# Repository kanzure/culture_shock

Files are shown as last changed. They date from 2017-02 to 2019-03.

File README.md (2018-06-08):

Table of Contents
=================

* [This repository documents how to use and make an electroporator.](#this-repository-documents-how-to-use-and-make-an-electroporator)
* [Now to describe the project directory and how to use it.](#now-to-describe-the-project-directory-and-how-to-use-it)
* [The Project Schematic Representation](#the-project-schematic-representation)
* [The Project Physical Design Representation](#the-project-physical-design-representation)
* [Running code on the Culture Shock platform(s)](#running-code-on-the-culture-shock-platforms)
* [Project Module Standard](#project-module-standard)
* [Using Culture Shock and Steps Leading up to Transformation](#using-culture-shock-and-steps-leading-up-to-transformation)
* [Aiding with Development and Debug](#aiding-with-development-and-debug)
* [Miscellany](#miscellany)

## This repository documents how to use and make an electroporator.

Cloning this repo gives you [ documentation on lab technique ](LAB_MANUAL.md) and [using culture shock,](USING_CULTURE_SHOCK.md) plus a project directory for making printed circuits
and related parts of an **electroporator**, a machine for transforming bacterial suspensions in water to become a new GMO.  For how to use culture shock, see [Using Culture Shock and Steps Leading up to Transformation](#using-culture-shock-and-steps-leading-up-to-transformation).  For how to make your own, or something new based on Culture Shock hardware, read on below.

The **culture shock** electroporator needs some care in using to avoid electrocution hazards -- it may not work out to borrow just some of this project and turn it on -- it really needs its insulating housing to be safe.

## Now to describe the project directory and how to use it.
You will notice files that end with .lht or .gvp .sch .bom.
Those hold the primary data to generate pcb fab files, or to reuse the circuits to make something else with this as a starting point.  

## The Project Schematic Representation
The schematic representations of the printed circuits that make up culture shock are edited with the **gschem program** from the free open source software, (FOSS), project called gEDA   Schematic files end in **.sch,** -- for example kvboard.sch.
* howtos here: [http://wiki.evilmadscientist.com/GEDA_Resources](http://wiki.evilmadscientist.com/GEDA_Resources)
* and [http://wiki.geda-project.org/geda:documentation](http://wiki.geda-project.org/geda:documentation)

## The Project Physical Design Representation
The **.lht files** hold layout data edited with the **pcb-rnd** FOSS program from here:  
	http://repo.hu/projects/pcb-rnd/	
If it's your first time using pcb or pcb-rnd, start from the begining with this tutorial for **pcb**, which **pcb-rnd** is derived from:  
	http://www.delorie.com/pcb/docs/gs/gs.html
	
To take a *quick look* at the state of things without needing to learn to edit them, you can look at image files of the schematics and layout with any browser.
Look in directory hardware_schematics_layouts for these files:  kvboard.lht.png kvboard.sch.png pyflex_f401.sch.png pyflex_f401.lht pyflex_f401_boost.sch.png.
To get ability to zoomin and also edit the schematics and layout, install the software as below on a debian testing installation.  It can be easy to start using those schematic and pcb editors -- just give these commands:

```bash
sudo apt-get update
sudo apt-get install geda
sudo apt-get install pcb-rnd
```

then run these commands from the project subdirectory hardware_schematics_layouts created by cloning the **culture shock** repo:
```bash
pcb-rnd kvboard.lht
pcb-rnd micropulser.lht
gschem kvboard.sch micropulser.sch
```
The schematic and netlist and layout tools used are from the gEDA code: http://wiki.evilmadscientist.com/GEDA_Resources#Basics

## Running code on the Culture Shock platform(s)
There are two MCU platforms now -- G30TH is phasing out of use, and PYFLEX_F401 is starting up:
* a board called g30pulser.sch runs with the micropython platform definition called G30TH
  * [Instructions to flash MicroPython for the G30TH version of culture_shock are here](DEVELOPER_NOTE.md#flashing-micropython)
  * [Additional notes are here (TODO: compress into a single document)](micropython_STM32F4_coding/micropython_compile_G30TH.txt)
* and a board called pyflex_f401.sch runs with the micropython platform definition called PYFLEX_F401.
  * PYFLEX_F401 is complete now, so compile micropython with platform PYFLEX_F401.
  * Very soon, instructions for compiling microptyhon programs for culture shock's PYFLEX_F401 platform will be written.

When you connect the culture_shock USB cable to your computer, it will now appear as a "USB mass storage" device.
Now you can simply copy the Python (.py) files to the "USB mass storage" drive/folder.
* For G30TH based copy the .Py files here: [g30_mcu_code](g30_mcu_code) 

The PYFLEX_F401 platform for micropython has the **STM32F401CE** MCU
* voltage converter from USB 5V or battery 3.2 volts up to 18VDC
* voltage converter from USB 5V down to lithium iron phosphate battery charging at 3.2 volts.
* 2 20 pin flat flex connectors to get to the GPIOs, ADCs, battery and com ports of the MCU
* a microUSB AB connector for charging
* a microUSB AB connector for development and data logging data transfer
* A 2-wire I2C port can be used with OLED and LCD displays.
* planned mode to precharge ONBOARD_18V and be ready tp fire a shot, then go back to standby after a minute. (not implemented yet)

## Project Module Standard
Flat flex cables, (FFCs), can be symmetric, their connectors are symmetric, and so connection signal vs. pin number order can be reversed by ordinary use of cables and connectors.  Using symmetric straight through flat flex cables and connectors is the standard for this project because it simplifies early design prototypes by allowing them to lay flat on the bench with component side of all modules up where one can see and probe them.  What symmetric and straight through means by example is: starting with a FFC connector with pins 1 thru 20 with a dot near pin 1 signals connect to another board by going through pin 1 on the first board, straight across without cables being folded or flipped over and into pin 20 of the other board. Pin 2 of the FFC connector on the first board leads to pin 19 on the 2nd, etc.

## Using Culture Shock and Steps Leading up to Transformation
Prepare growth media, purify plasmid DNA from a bacterial culture -- [Lab Manual.md](LAB_MANUAL.md), then transform E.Coli by electroporation -- [ Using Culture Shock](USING_CULTURE_SHOCK.md).

## Aiding Development and Debugging
See [Developer's Manual](DEVELOPER_NOTE.md) to get started with the culture shock and micropython GIT repositories on github, and hook up to culture shock so you can give it commands.

## Miscellany
The repo's `.gitignore` file is set to skip git tracking of `.jpg` (photos) and `.pdf` (datasheets) and zipped file bundles, so any of them to distribute need to be saved outside the git repo as a zip file.

Seeing a preview of markdown files like this README.md helps speed documenation.  This previewer is useful:  [grip markdown viewer](https://github.com/joeyespo/grip)  Grip can serve more than one file at a time with this syntax:  grip README.md 6150  grip LAB_MANUAL.md 6151.  Doing that helps edit files like this one, (with many links to other files).

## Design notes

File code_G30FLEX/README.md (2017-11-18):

First, before starting, the MCU board must have micropython loaded -- see other docs 
such as micropython_compile_G30TH.txt, micropython_coding_with_rshell.txt about that.

To run code on a culture shock board, (with STM32F401 inside), several files are needed.

As this code is written so far, it needs these files loaded to the flash filesystem of the 
micropython running MCU:

* tim3_enable_tim1_tim2_tim5__tim1_shuts_down.py
* stm_low_level.py
* nvic.py
* boot.py
* ssd1306.py
  * (__OPTIONAL__) for 0.96" 128x64 OLED support

After loading those files and resetting the MCU board, the tim3_enable_tim1_tim2_tim5__tim1_shuts_down.py
program will run.

For a serial prompt:
 - Windows: you need to go to 'Device manager', right click on the unknown device,
   then update the driver software, using the 'pybcdc.inf' file found on this drive.
   Then use a terminal program like Hyperterminal or putty.
 - Mac OS X: use the command: screen /dev/tty.usbmodem*
 - Linux: use the command: screen /dev/ttyACM0

Please visit http://micropython.org/help/ for further help.

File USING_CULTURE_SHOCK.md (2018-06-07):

# Using Culture Shock v0.5 first article prototype
###  Intro
  The  v0.5 first article prototype has  no buttons -- all commands are done via a command line over the USB serial port.  
  New scripts to run are loaded by writing files to the culture shock using the USB port virtual file system files located at:
  * Windows, Linux, Mac: folder called PYBFLASH in the popup window for a USB drive when culture shock data USB cable plug is plugged into the USB port of a laptop.

  * Debian Linux:  /username/media/PYBFLASH directory

The project github repository, (that this document is part of), is the source of scripts to run for basic testing and as a starting point for your new recipes. The folder to find code in is: [code_PYFLEX_F401  ](https://github.com/kanzure/culture_shock/tree/master/code_PYFLEX_F401    "Culture Shock micropython code")   

####

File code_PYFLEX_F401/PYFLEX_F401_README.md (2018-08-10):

First, before starting, the MCU board must have micropython loaded -- see other docs 
such as micropython_compile_G30TH.txt, micropython_coding_with_rshell.txt about that.

To run code on a culture shock board, (with STM32F401 inside), several files are needed.

As this code is written for v0.5 hardware, it needs these files loaded to the flash filesystem of the 
micropython running MCU:

* pulser_main.py
* stm_low_level.py
* nvic.py
* boot.py
* ssd1306.py
  * (__OPTIONAL__) for 0.96" 128x64 OLED support

After loading those files and resetting the MCU board, the program called by boot.py will run.

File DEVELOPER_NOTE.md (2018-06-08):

Table of Contents
=================

* [GIT workflow methods](#git-workflow-methods)
  * [Setting up your GIT clone with collaborators:](#setting-up-your-git-clone-with-collaborators)
  * [reset a collaborator's master to kanzure's master](#reset-a-collaborators-master-to-kanzures-master)
  * [Merging branches (will usually leave a "merge commit" which rebasing can avoid)](#merging-branches-will-usually-leave-a-merge-commit-which-rebasing-can-avoid)
  * [Rebasing branches](#rebasing-branches)
     * [Squashing commits with rebase](#squashing-commits-with-rebase)
  * [Setup better git difftool/mergetool](#setup-better-git-difftoolmergetool)
* [Creating table-of-contents for MarkDown (.md) files](#creating-table-of-contents-for-markdown-md-files)
* [Preview MarkDown files locally before commit/push to GitHub](#preview-markdown-files-locally-before-commitpush-to-github)
* [Getting a micropython prompt on the USB serial port](#getting-a-micropython-prompt-on-the-usb-serial-port)
* [Self-Test Idea](#self-test-idea)
  * [Debug setup](#debug-setup)
  * [ADC pulse viewer GUI](#adc-pulse-viewer-gui)
  * [ADC graphing on OLED display](#adc-graphing-on-oled-display)
* [MicroPython C Modules](#micropython-c-modules)
* [Flashing MicroPython](#flashing-micropython)
  * [G30TH](#g30th)
* [ADC DMA ideas](#adc-dma-ideas)
  * [STM selected documentation](#stm-selected-documentation)
  * [Registers](#registers)
     * [11.12.1 ADC status register (ADC_SR)](#11121-adc-status-register-adc_sr)
     * [11.12.2 ADC control register 1 (ADC_CR1)](#11122-adc-control-register-1-adc_cr1)
     * [11.12.3 ADC control register 2 (ADC_CR2)](#11123-adc-control-register-2-adc_cr2)

# GIT workflow methods
## Setting up your GIT clone with collaborators:
* Adding a collaborator's github URL
  * ```bash
    git remote add collaborator https://github.com/<collaborator_username>/culture_shock.git
    git fetch collaborator
    ```

## reset a collaborator's master to kanzure's master
based on this StackOverflow (https://stackoverflow.com/a/39628366/253127)

* add the original (kanzure's) repo:
  * `git remote add original https://github.com/kanzure/culture_shock.git`
* Fetch the latest changes from the collaborator
  * `git fetch original`
* Checkout your __local__ master branch
  * `git checkout master`
* reset master to original's version, so your files match theirs exactly
  * `git reset --hard original/master`

## Merging branches (will usually leave a "merge commit" which rebasing can avoid)
* Fetch the latest changes from the collaborator
  * `git fetch collaborator`
* Merge the collaborator's changes (from master branch)
  * `git merge collaborator/master`

## Rebasing branches 
* Fetch the latest changes from the collaborator
  * `git fetch collaborator`
* Checkout the collaborator's changes (from master branch)
  * `git checkout collaborator/master`
* Depending on if merge conflicts are expected
  * If not, then use __non-interactive__ rebasing
    * `git rebase master`
  * If yes (or you want to squash/edit their commits/commit-messages), then use __interactive__ rebasing
    * `git rebase -i master`
* If there are merge conflicts
  * show the files in question
    * `git status`
  * use git's mergetool to see the your changes and their changes side-by-side
    * single file
      * `git mergetool path/to/file_of_interest`
    * all files in question
      * `git mergetool`
* Create a temporary branch for safety
  * `git checkout -b mergeme`
* Go back to __your__ last version of __master__ branch
  * `git checkout master`
* Merge your rebased changes into master
  * `git merge mergeme`

### Squashing commits with rebase
* I am currently using this method during debugging of the MarkDown syntax used for this note
  * ```
    git add DEVELOPER_NOTE.md
    git commit -m "sqsh"
    git rebase -i HEAD~2
    ```
* the last command allows you to modify whether the last (2) commits are applied, how they are applied, in what order
* I see the following output
  * ```
    pick 12e8eee added notes for syncing with other github 'forks' (collaborators)
    pick 7f7aedb sqsh
    
    # Rebase aebf933..7f7aedb onto aebf933 (2 command(s))
    #
    # Commands:
    # p, pick = use commit
    # r, reword = use commit, but edit the commit message
    # e, edit = use commit, but stop for amending
    # s, squash = use commit, but meld into previous commit
    # f, fixup = like "squash", but discard this commit's log message
    # x, exec = run command (the rest of the line) using shell
    # d, drop = remove commit
    #
    # These lines can be re-ordered; they are executed from top to bottom.
    #
    # If you remove a line here THAT COMMIT WILL BE LOST.
    #
    # However, if you remove everything, the rebase will be aborted.
    #
    # Note that empty commits are commented out
    ```
* I would then edit the second line to read
  * `s 7f7aedb sqsh`
  * This squashes the commit into the previous (commit above it)
    * the goal is to merge the commit-contents into the previous commit, but hide the fact that the contents actually came from more than one commit (squashing all changes into a single commit)
* save the text file
* now rebase will open the commit-message, showing all the combined messages
  * ```
    # This is a combination of 2 commits.
    # The first commit's message is:
    
    added notes for syncing with other github 'forks' (collaborators)
    
    # This is the 2nd commit message:
    
    sqsh
    
    # Please enter the commit message for your changes. Lines starting
    # with '#' will be ignored, and an empty message aborts the commit.
    # interactive rebase in progress; onto 7120033
    # Last commands done (2 commands done):
    #    pick 3a59de4 added notes for syncing with other github 'forks' (collaborators)
    #    s 63cf084 sqsh
    # No commands remaining.
    # You are currently rebasing branch 'master' on '7120033'.
    #
    # Changes to be committed:
    #       modified:   DEVELOPER_NOTE.md
    ```
  * remove the line starting with
    * `sqsh`
* save and exit the commit-message
* Done!
  * continue working, push, etc
    * during this debug cycle, because I continually edit the MarkDown, then squash, to test the web-browser rendering I then have to run a `git push -f` to force-push and overwrite the previous commit I made, because it was already made public

## Setup better git difftool/mergetool
* What look to be pretty good notes here:
  * https://gist.github.com/karenyyng/f19ff75c60f18b4b8149#file-git_mergetool_tutorial-md
* Setting a specific mergetool/difftool which is already supported by git
  * from: https://stackoverflow.com/a/6412645/253127
  * example of open-source tools supported
    * kdiff3, kompare, tkdiff, meld, xxdiff, emerge, vimdiff, gvimdiff, ecmerge, diffuse, opendiff, p4merge and araxis
  * add the following lines to your `~/.gitconfig`
    * ```
      [diff]
          tool = meld
      ```
* Setting up mergetool/difftool that isn't supported
  * the stackoverflow linked from the prev also works, but looks to be a less-concise copy of this
    * see "Git 1.7.x and older" section
      * https://www.scootersoftware.com/support.php?zz=kb_vcs#gitlinux

# Creating table-of-contents for MarkDown (.md) files
* get this handy TOC generator
  * `git clone https://github.com/ekalinin/github-markdown-toc`
* cd to the __culture_shock__ repo, then run the TOC generator on the .md file of interest
  * `cd culture_shock`
  * `../github-markdown-toc/gh-md-toc DEVELOPER_NOTE.md`
* paste the output into the .md file
* commit and push

# Preview MarkDown files locally before commit/push to GitHub
* Download `grip` with `pip`
  * `pip install grip`
    * source https://github.com/joeyespo/grip
* `cd` to __culture_shock__ repo
* run `grip`
  * copy the web URL printed on the terminal
    * navigate to it using your web-browser

# Getting a micropython prompt on the USB serial port:
 - Windows: you need to go to 'Device manager', right click on the unknown device,
   then update the driver software, using the 'pybcdc.inf' file found on this drive.
   Then use a terminal program like Hyperterminal or putty.
 - Mac OS X: use the command: screen /dev/tty.usbmodem*
 - Linux: use the command: screen /dev/ttyACM0

 - After you have a prompt, you can tell culture shock to do a soft reset \<ctl\>d or \<ctl\>x to get out of the REPL (read eval print loop) and back to your system command line.  For more on what micropython can do from the REPL, see http://micropython.org/help/ as a starting point.

# Self-Test Idea
* Setup 10 pulses with shortest possible pulse-width
  * setup list `adc_vals`
* Setup ADC timer with same freq as pulses, but out of phase 180°
* setup IRQ function callback on ADC timer, the function will:
  * read the ADC, append to `adc_vals`
* at end of pulse-train, send `adc_vals` out the serial port for printing on the user-terminal

## Debug setup
* PA0 and PA1, as seen here in kvboard v0.1, are the wires for pulsing the switched power supply to get high volts.
![alt text](https://raw.githubusercontent.com/kanzure/culture_shock/0ed7805f742bc01429d4466670109e092e9572f7/hardware_schematics_layouts/kvboard.png "KiloVolt producing circuit-board v0.1 (2017-2-16)")
* Connect your oscilloscope to these pins to watch the pulse widths and periods of each digital operation from the microcontroller
  * These are useful to trigger on
    * you can then watch the analog/choppier high-voltage develop on another oscilloscope input
* With Culture_Shock v0.1, the G30TH module was used for the STM microcontroller it was built with
  * The pinout of the G30TH module is shown here on the right-side
![alt](photos_protos_tests_simuls_sketches/G30TH_module_schematic_PCB_pinout.jpg)
* Connecting the first oscilloscope probe to PA1 and GND (red minigrabber)
  ![alt](photos_protos_tests_simuls_sketches/probing_g30th_pa1_gnd.jpg)
* Connecting the second oscilloscope probe to PA0
  ![alt](photos_protos_tests_simuls_sketches/probing_g30th_pa1_pa0_gnd.jpg)
* Connecting the third oscilloscope probe and 1GOhm resistor to the high-voltage (HV) output
  * 33 kOhm dummy load is used between the HV terminals
  ![alt](photos_protos_tests_simuls_sketches/probing_33k_dummy_load_with_1GOhm.jpg)
* Overall setup
  ![alt](photos_protos_tests_simuls_sketches/probing__overall_setup.jpg)

## ADC pulse viewer GUI
* requires pexpect `pip install pexpect` and tk (comes with Python out-of-box in most cases)
  * pexpect is a terminal interaction library
    * you can send lines to a terminal
    * you setup what you expect the terminal to reply with
      * these act like triggers to tell your program your output was seen
* I used `picocom` for test and development
  * thus what I programmed the <b>expect</b>ations to be might need adjusted for other terminal programs
* the terminal interaction is logged to the command-line where you start the GUI
  * use this to debug why your <b>expect</b>ations aren't being met
* every time the __pulse__ button is clicked, the __a()__ function is called using the 3 input boxes for args
  * reduce the __Num Pulse Pairs__ for a first-try adjustment
    * you should see the waveform get shorter in length
* __NOTE__: this __is__ still __work-in-progress__, dependent on the ADC working, which is still WIP
  * has not been rigourously debugged, understood, or tested with conditions other than the default (starting) conditions for period, width, num-pulses

* see demo pics here
  * https://imgur.com/a/I3CLt
![alt text](https://i.imgur.com/1TSNEN3.gif "ADC reporting waveform to GUI")

## ADC graphing on OLED display
* https://github.com/micropython/micropython/blob/master/drivers/display/ssd1306.py
  * http://docs.micropython.org/en/latest/wipy/library/machine.I2C.html
  * http://docs.micropython.org/en/latest/pyboard/library/framebuf.html
* Graphing the ADC values will require scaling the data to fit.
* Currently with the DMA transfer the ADC reads into a buffer of length 2048.
* The OLED is only 128 wide
  * 64 tall
* scaling in the X direction may be done with averaging every (2048/128)==16 values
  * or a median filter
  * or a max-val filter
* scaling in the Y will use the ADC max-val and the height of the OLED (64)
  * val / 1024.0 * 64.0

* see demo pics here
  * https://imgur.com/a/LBorg

# MicroPython C Modules
In case we really need to customize or reduce overhead
* http://micropython-dev-docs.readthedocs.io/en/latest/adding-module.html

# Flashing MicroPython
## G30TH
* See here for background
  * http://blog.davehylands.com/2016/07/bringing-up-micropython-on-ghi.html
* `git clone https://github.com/micropython/micropython.git`
* `cd micropython`
* `git checkout v1.9.3`
* __patch with ADC DMA sampling changes__
  * `patch -p1 ./ports/stm32/adc.c < ../culture_shock/FOR_ADC_DMA__adc.c.patch`
    * assumes culture_shock and micropython repos are in the same directory
    * hacks the __read_timed__ method, and adds a new method __read_timed_stop__
* `cd ports/stm32/boards/`
* `git clone https://github.com/dhylands/G30TH.git`
* `cd ..`
* connect 3.3V to pin B0
* `make BOARD=G30TH`
* if you need to erase the program area, i.e. if you wrote bad MicroPython code that "bricked" the MCU
  * `dfu-util -v -s :mass-erase:force -a 0 -d 0483:df11 -D build-G30TH/firmware.dfu`
* `make BOARD=G30TH deploy`

# ADC DMA ideas

## STM selected documentation
* 11.8.1 Using the DMA
When the DMA mode is enabled (DMA bit set to 1 in the ADC_CR2 register), after each
conversion of a regular channel, a DMA request is generated. This allows the transfer of the
converted data from the ADC_DR register to the destination location selected by the
software.
Despite this, if data are lost (overrun), the OVR bit in the ADC_SR register is set and an
interrupt is generated (if the OVRIE enable bit is set). DMA transfers are then disabled and
DMA requests are no longer accepted. In this case, if a DMA request is made, the regular
conversion in progress is aborted and further regular triggers are ignored. It is then
necessary to clear the OVR flag and the DMAEN bit in the used DMA stream, and to re-
initialize both the DMA and the ADC to have the wanted converted channel data transferred
to the right memory location. Only then can the conversion be resumed and the data
transfer, enabled again.

## Registers
### 11.12.1 ADC status register (ADC_SR)
5     4     3     2     1     0
OVR   STRT  JSTRT JEOC  EOC   AWD
rc_w0 rc_w0 rc_w0 rc_w0 rc_w0 rc_w0

* Bits 31:6 Reserved, must be kept at reset value.
* Bit 5 OVR: Overrun
  * This bit is set by hardware when data are lost . It is cleared by software. Overrun detection is enabled only when DMA = 1 or EOCS = 1.
    * 0: No overrun occurred
    * 1: Overrun has occurred
* Bit 4 STRT: Regular channel start flag
  * This bit is set by hardware when regular channel conversion starts. It is cleared by software.
    * 0: No regular channel conversion started
    * 1: Regular channel conversion has started
* Bit 3 JSTRT: Injected channel start flag
  * This bit is set by hardware when injected group conversion starts. It is cleared by software.
    * 0: No injected group conversion started
    * 1: Injected group conversion has started
* Bit 2 JEOC: Injected channel end of conversion
  * This bit is set by hardware at the end of the conversion of all injected channels in the group. It is cleared by software.
    * 0: Conversion is not complete
    * 1: Conversion complete
* Bit 1 EOC: Regular channel end of conversion
  * This bit is set by hardware at the end of the conversion of a regular group of channels. It is cleared by software or by reading the ADC_DR register.
    * 0: Conversion not complete (EOCS=0), or sequence of conversions not complete (EOCS=1)
    * 1: Conversion complete (EOCS=0), or sequence of conversions complete (EOCS=1)
* Bit 0 AWD: Analog watchdog flag
  * This bit is set by hardware when the converted voltage crosses the values programmed in the ADC_LTR and ADC_HTR registers. It is cleared by software.
    * 0: No analog watchdog event occurred
    * 1: Analog watchdog event occurred

### 11.12.2 ADC control register 1 (ADC_CR1)
* Address offset: 0x04
* Reset value: 0x0000 0000

* Bit 31 Reserved, must be kept at reset value.
* Bit 30 SWSTART: Start conversion of regular channels
  * This bit is set by software to start conversion and cleared by hardware as soon as the conversion starts.
    * 0: Reset state
    * 1: Starts conversion of regular channels
  * Note: This bit can be set only when ADON = 1 otherwise no conversion is launched.
* Bits 29:28 EXTEN: External trigger enable for regular channels
  * These bits are set and cleared by software to select the external trigger polarity and enable the trigger of a regular group.
    * 00: Trigger detection disabled
    * 01: Trigger detection on the rising edge
    * 10: Trigger detection on the falling edge
    * 11: Trigger detection on both the rising and falling edges
* Bits 27:24 EXTSEL[3:0]: External event select for regular group
  * These bits select the external event used to trigger the start of conversion of a regular group:
    * 0000: Timer 1 CC1 event
    * 0001: Timer 1 CC2 event
    * 0010: Timer 1 CC3 event
    * 0011: Timer 2 CC2 event
    * 0100: Timer 2 CC3 event
    * 0101: Timer 2 CC4 event
    * 0110: Timer 2 TRGO event
    * 0111: Timer 3 CC1 event
    * 1000: Timer 3 TRGO event
    * 1001: Timer 4 CC4 event
    * 1010: Timer 5 CC1 event
    * 1011: Timer 5 CC2 event
    * 1100: Timer 5 CC3 event
    * 1101: Reserved
    * 1110: Reserved
    * 1111: EXTI line11
* Bit 23 Reserved, must be kept at reset value.
* Bit 22 JSWSTART: Start conversion of injected channels
  * This bit is set by software and cleared by hardware as soon as the conversion starts.
    * 0: Reset state
    * 1: Starts conversion of injected channels
  * Note: This bit can be set only when ADON = 1 otherwise no conversion is launched.
* Bits 21:20 JEXTEN: External trigger enable for injected channels
  * These bits are set and cleared by software to select the external trigger polarity and enable the trigger of an injected group.
    * 00: Trigger detection disabled
    * 01: Trigger detection on the rising edge
    * 10: Trigger detection on the falling edge
    * 11: Trigger detection on both the rising and falling edges
* Bits 19:16 JEXTSEL[3:0]: External event select for injected group
  * These bits select the external event used to trigger the start of conversion of an injected group.
    * 0000: Timer 1 CC4 event
    * 0001: Timer 1 TRGO event
    * 0010: Timer 2 CC1 event
    * 0011: Timer 2 TRGO event
    * 0100: Timer 3 CC2 event
    * 0101: Timer 3 CC4 event
    * 0110: Timer 4 CC1 event
    * 0111: Timer 4 CC2 event
    * 1000: Timer 4 CC3 event
    * 1001: Timer 4 TRGO event
    * 1010: Timer 5 CC4 event
    * 1011: Timer 5 TRGO event
    * 1100: Reserved
    * 1101: Reserved
    * 1110: Reserved
    * 1111: EXTI line15
* Bits 15:12 Reserved, must be kept at reset value.
* Bit 11 ALIGN: Data alignment
  * This bit is set and cleared by software. Refer to Figure 35 and Figure 36.
    * 0: Right alignment
    * 1: Left alignment
* Bit 10 EOCS: End of conversion selection
  * This bit is set and cleared by software.
    * 0: The EOC bit is set at the end of each sequence of regular conversions. Overrun detection is enabled only if DMA=1.
    * 1: The EOC bit is set at the end of each regular conversion. Overrun detection is enabled.
* Bit 9 DDS: DMA disable selection (for single ADC mode)
  * This bit is set and cleared by software.
    * 0: No new DMA request is issued after the last transfer (as configured in the DMA controller)
    * 1: DMA requests are issued as long as data are converted and DMA=1
* Bit 8 DMA: Direct memory access mode (for single ADC mode)
  * This bit is set and cleared by software. Refer to the DMA controller chapter for more details.
    * 0: DMA mode disabled
    * 1: DMA mode enabled
* Bits 7:2 Reserved, must be kept at reset value.
* Bit 1 CONT: Continuous conversion
  * This bit is set and cleared by software. If it is set, conversion takes place continuously until it is cleared.
    * 0: Single conversion mode
    * 1: Continuous conversion mode
* Bit 0 ADON: A/D Converter ON / OFF
  * This bit is set and cleared by software.
  * Note:
    * 0: Disable ADC conversion and go to power down mode
    * 1: Enable ADC

### 11.12.3 ADC control register 2 (ADC_CR2)
* Address offset: 0x08
* Reset value: 0x0000 0000
* Bit 31 Reserved, must be kept at reset value.
* Bit 30 SWSTART: Start conversion of regular channels
  * This bit is set by software to start conversion and cleared by hardware as soon as the conversion starts.
    * 0: Reset state
    * 1: Starts conversion of regular channels
  * Note: This bit can be set only when ADON = 1 otherwise no conversion is launched.
* Bits 29:28 EXTEN: External trigger enable for regular channels
  * These bits are set and cleared by software to select the external trigger polarity and enable the trigger of a regular group.
    * 00: Trigger detection disabled
    * 01: Trigger detection on the rising edge
    * 10: Trigger detection on the falling edge
    * 11: Trigger detection on both the rising and falling edges
* Bits 27:24 EXTSEL[3:0]: External event select for regular group
  * These bits select the external event used to trigger the start of conversion of a regular group:
    * 0000: Timer 1 CC1 event
    * 0001: Timer 1 CC2 event
    * 0010: Timer 1 CC3 event
    * 0011: Timer 2 CC2 event
    * 0100: Timer 2 CC3 event
    * 0101: Timer 2 CC4 event
    * 0110: Timer 2 TRGO event
    * 0111: Timer 3 CC1 event
    * 1000: Timer 3 TRGO event
    * 1001: Timer 4 CC4 event
    * 1010: Timer 5 CC1 event
    * 1011: Timer 5 CC2 event
    * 1100: Timer 5 CC3 event
    * 1101: Reserved
    * 1110: Reserved
    * 1111: EXTI line11
* Bit 23 Reserved, must be kept at reset value.
* Bit 22 JSWSTART: Start conversion of injected channels
  * This bit is set by software and cleared by hardware as soon as the conversion starts.
    * 0: Reset state
    * 1: Starts conversion of injected channels
  * Note: This bit can be set only when ADON = 1 otherwise no conversion is launched.
* Bits 21:20 JEXTEN: External trigger enable for injected channels
  * These bits are set and cleared by software to select the external trigger polarity and enable the trigger of an injected group.
    * 00: Trigger detection disabled
    * 01: Trigger detection on the rising edge
    * 10: Trigger detection on the falling edge
    * 11: Trigger detection on both the rising and falling edges
* Bits 19:16 JEXTSEL[3:0]: External event select for injected group
  * These bits select the external event used to trigger the start of conversion of an injected group.
    * 0000: Timer 1 CC4 event
    * 0001: Timer 1 TRGO event
    * 0010: Timer 2 CC1 event
    * 0011: Timer 2 TRGO event
    * 0100: Timer 3 CC2 event
    * 0101: Timer 3 CC4 event
    * 0110: Timer 4 CC1 event
    * 0111: Timer 4 CC2 event
    * 1000: Timer 4 CC3 event
    * 1001: Timer 4 TRGO event
    * 1010: Timer 5 CC4 event
    * 1011: Timer 5 TRGO event
    * 1100: Reserved
    * 1101: Reserved
    * 1110: Reserved
    * 1111: EXTI line15
* Bits 15:12 Reserved, must be kept at reset value.
* Bit 11 ALIGN: Data alignment
  * This bit is set and cleared by software. Refer to Figure 35 and Figure 36.
    * 0: Right alignment
    * 1: Left alignment
* Bit 10 EOCS: End of conversion selection
  * This bit is set and cleared by software.
    * 0: The EOC bit is set at the end of each sequence of regular conversions. Overrun detection is enabled only if DMA=1.
    * 1: The EOC bit is set at the end of each regular conversion. Overrun detection is enabled.
* Bit 9 DDS: DMA disable selection (for single ADC mode)
  * This bit is set and cleared by software.
    * 0: No new DMA request is issued after the last transfer (as configured in the DMA controller)
    * 1: DMA requests are issued as long as data are converted and DMA=1
* Bit 8 DMA: Direct memory access mode (for single ADC mode)
  * This bit is set and cleared by software. Refer to the DMA controller chapter for more details.
    * 0: DMA mode disabled
    * 1: DMA mode enabled
* Bits 7:2 Reserved, must be kept at reset value.
* Bit 1 CONT: Continuous conversion
  * This bit is set and cleared by software. If it is set, conversion takes place continuously until it is cleared.
    * 0: Single conversion mode
    * 1: Continuous conversion mode
* Bit 0 ADON: A/D Converter ON / OFF
  * This bit is set and cleared by software.
  * Note:
    * 0: Disable ADC conversion and go to power down mode
    * 1: Enable ADC

 ### Remaining registers
 * [REGISTER INFO](REGISTER_INFO.md)

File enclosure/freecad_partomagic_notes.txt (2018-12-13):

 
    easyw-fc wrote:
    Hi, when using PoM I can only create nested Parts, but without the option to have more of one Part at the same level... may be I'm not using PoM in the right way...I attach the desired and of the PoM tree I get

PoM always adds whatever is created to active container. Including new Parts. That is, to have "Part002" to "Part", activate "Part" before creating "Part002" by double-clicking it in tree (you can also get there using Leave, Enter buttons of PoM workbench, which I highly recommend adding to a global toolbar, as they are quite versatile).

To add another Part to the root of document, deactivate whatever is active (either by double-clicking it in tree, or pressing Leave button until it becomes grey)

   triplus wrote:
    How about if Tip would have a Compound property. Once enabled Tip would basically become Part -> Make compound feature (making a compound out of individual features inside Module/Body)? I am guessing user could use all sorts of tools already mentioned earlier (and a few others) directly on such Module/Body after?

I'm making a special independent container for that. Do you think I should merge them all into one mighty container? (the benefit of doing that is ability to switch container type after it's been made and populated).
Top

    shaise wrote:
    Then what is the meaning of a Cube inside a Body? (create a cube in Part WB, select it, then press the Body button from PartDesign)

This process imports any type of solid as base feature in a PartDesign body, so you can use PD tools with it.

    shaise wrote:
    I still cant put sketches directly on it

Sure you can, but for some reason PartDesign still considers the cube a "foreign" object. So when trying to map a sketch to the cube, a dialog opens which says that selected geometries are not part of the active body, and to select a type of reference. The first two (Make independent copy/Make dependent copy) create a reference object, but "Create cross-reference" attaches the sketch directly to the cube.

by DeepSOIC » Mon Mar 06, 2017 2:33 pm 

Let's say you are modeling a flange, with a non-circular opening. Lets use a slot. We want screw holes around the opening... 
There is no PartDesign pattern (AFAIR) that can produce the necessary holes, but there is a handy tool in Draft workbench that can help, Draft PathArray. This is where PoM Subtractive Shape comes in.
* Create Subtractive shape container. You will be presented with an empty screen, where you should model the shape that cuts the holes.
* Add shapebinder of the sketch that was padded (select Sketch in tree, and click PoM Shapebinder).
* From Sketcher workbench, create a new sketch, and constrain up a slot that goes through the centers of future screwholes.
* From Part workbench, add a cylinder, and set it up to have the right radius, and enough height to penetrate all the way through. Leave it at the origin
* Select Cylinder, Sketch001, and apply Draft PathArray 
* Done! Leave the container to get back into Body (e.g. use PoM Leave command, or double-click Body in tree).
You may need to click Recompute button to see the result. Also, there is a chance Tip property of SubtractiveShape isn't pointing to the actual shape to use for cutting (PathArray). In that case, you can fix it by using PoM Set as Tip command. 

by DeepSOIC » Tue Mar 07, 2017 2:58 pm 
New feature!
* Exporter
It is an object you add to the project, and it can automatically export an object into a file whenever it changes. It can export Parts and Groups, but limited to a single level nesting (child Part containers are fed to FreeCAD's exporter, but FC's exporters usually ignore them).
I hope that this picture explains well what it does   https://forum.freecadweb.org/download/file.php?id=34489

Exporter checks that model has no features in an error state, will refuse to export if it finds errors.

BLUE = edits

New feature!
* Tree automation
When you enter a container, tree is automatically expanded to show only the stuff in active container. Everything around it is automatically collapsed.

For example. You are in shapegroup deep inside, and you change active container to body. shapegroup is automatically collapsed, and part001 is too, so that the tree view shows the piece you work on in isolation.

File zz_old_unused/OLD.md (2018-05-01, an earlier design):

Old and Unused Directories and Files
=================

* These are Files that were for temporary use in debugging, or somehow are obsolete.
    they might still be useful for supporting existing early prototypes, so this is where to 
    look in that case.

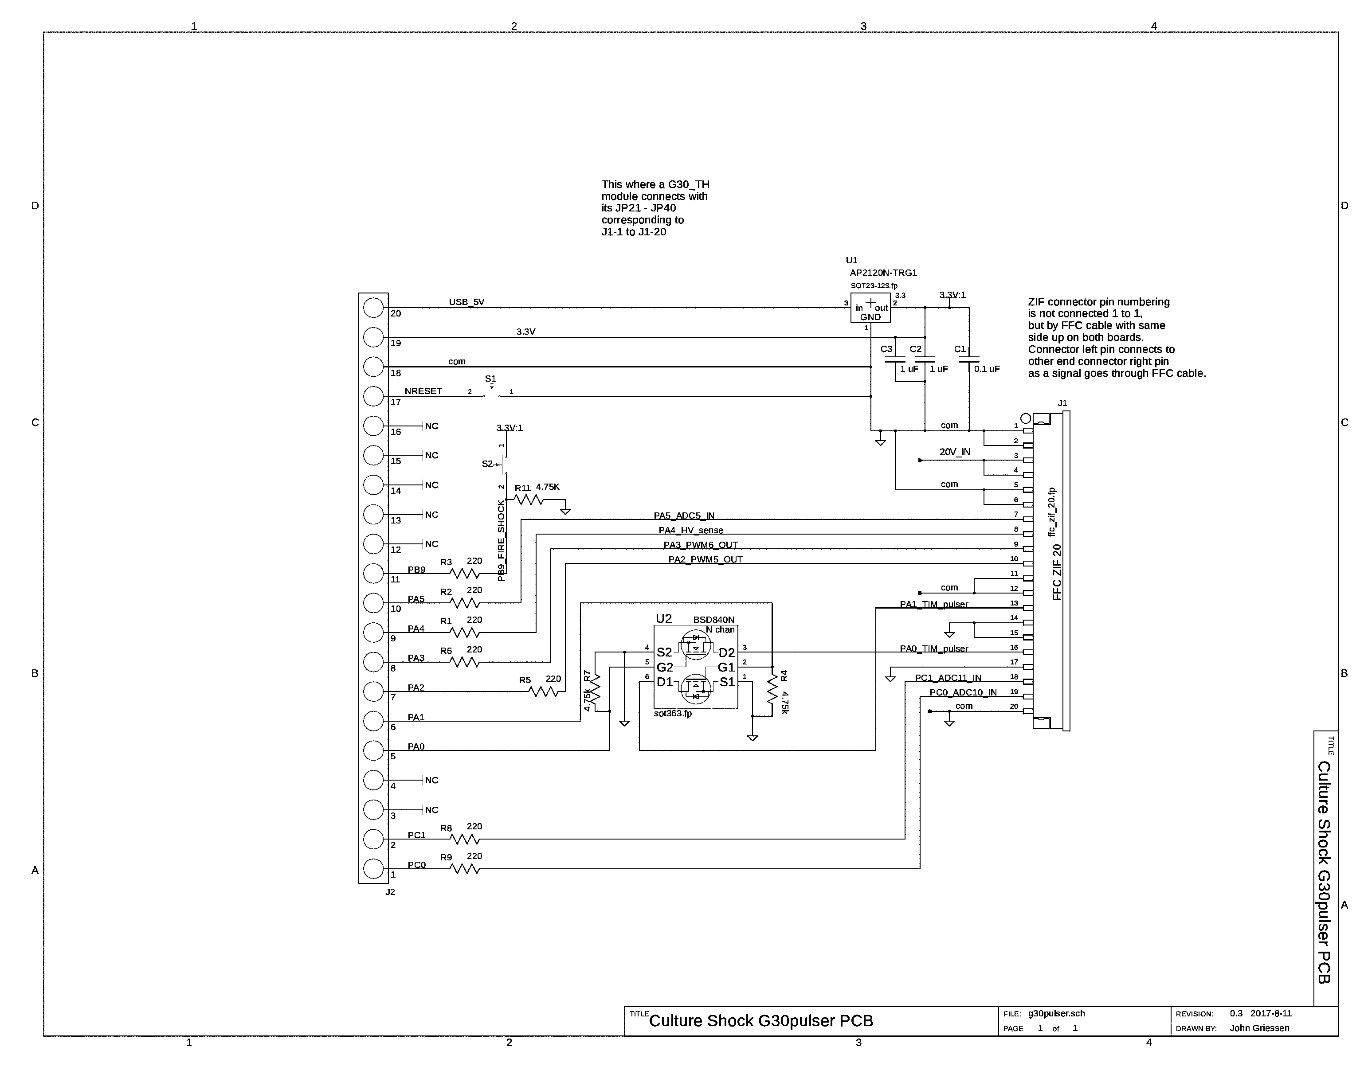
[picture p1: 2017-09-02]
hardware_schematics_layouts/g30pulser-sm.png

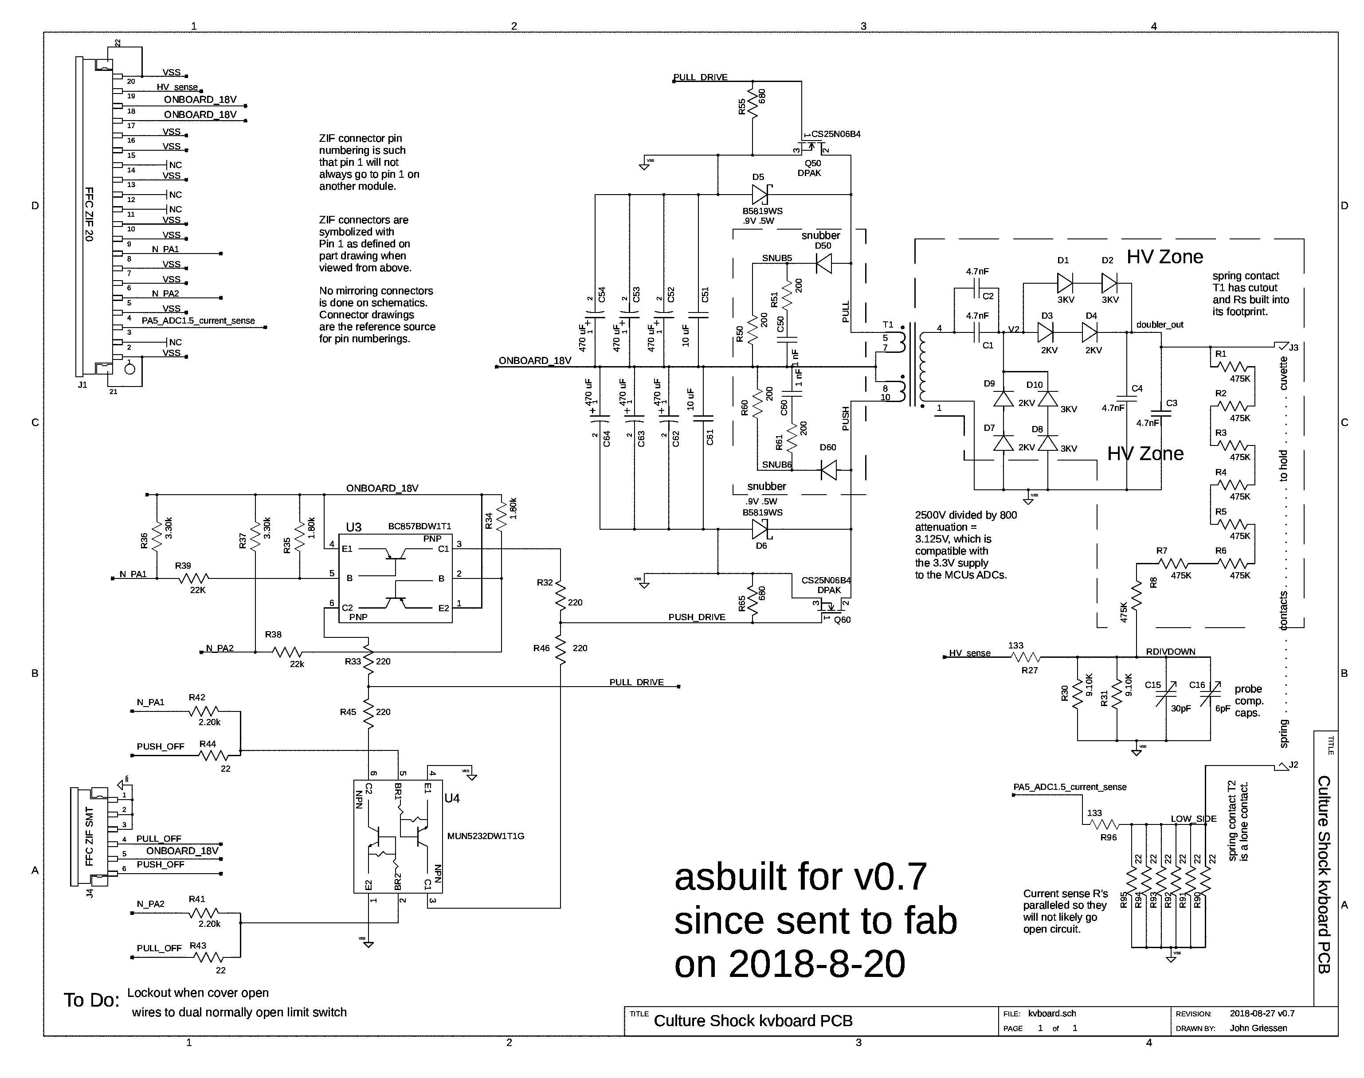
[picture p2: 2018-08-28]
hardware_schematics_layouts/kvboard_asbuilt_v0.7.sch-sm.png

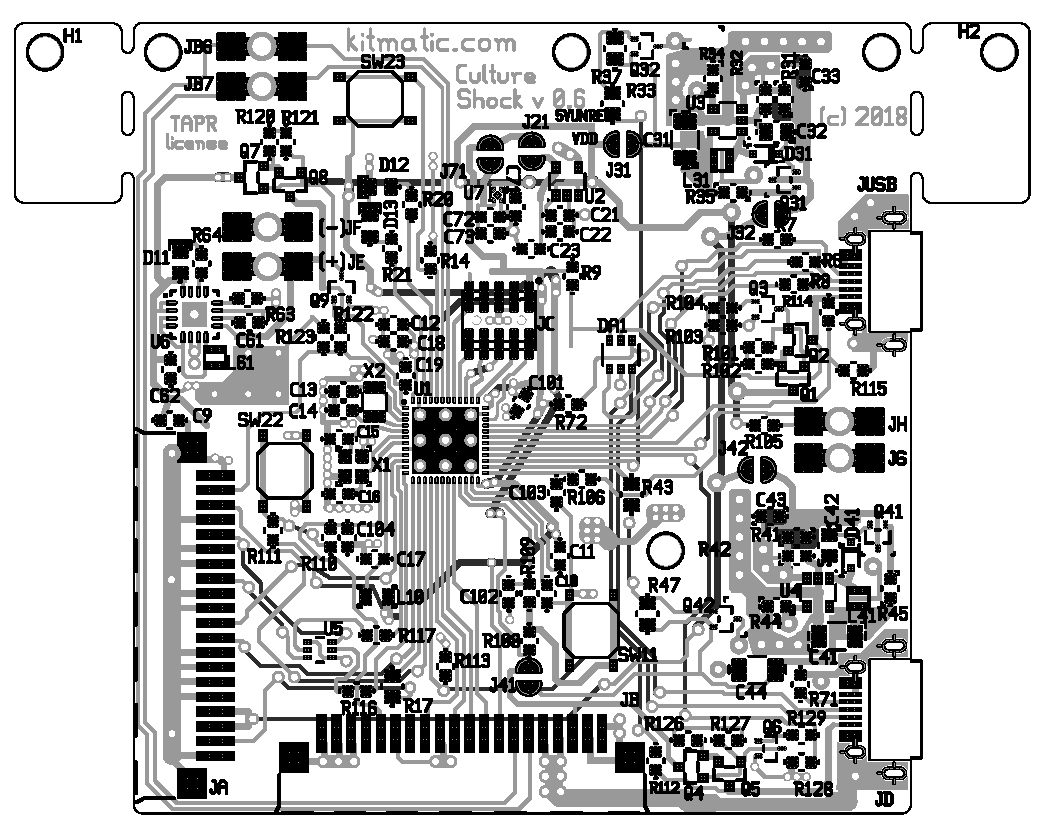
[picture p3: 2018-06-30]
hardware_schematics_layouts/pyflex_f401_v0.6_assy.png

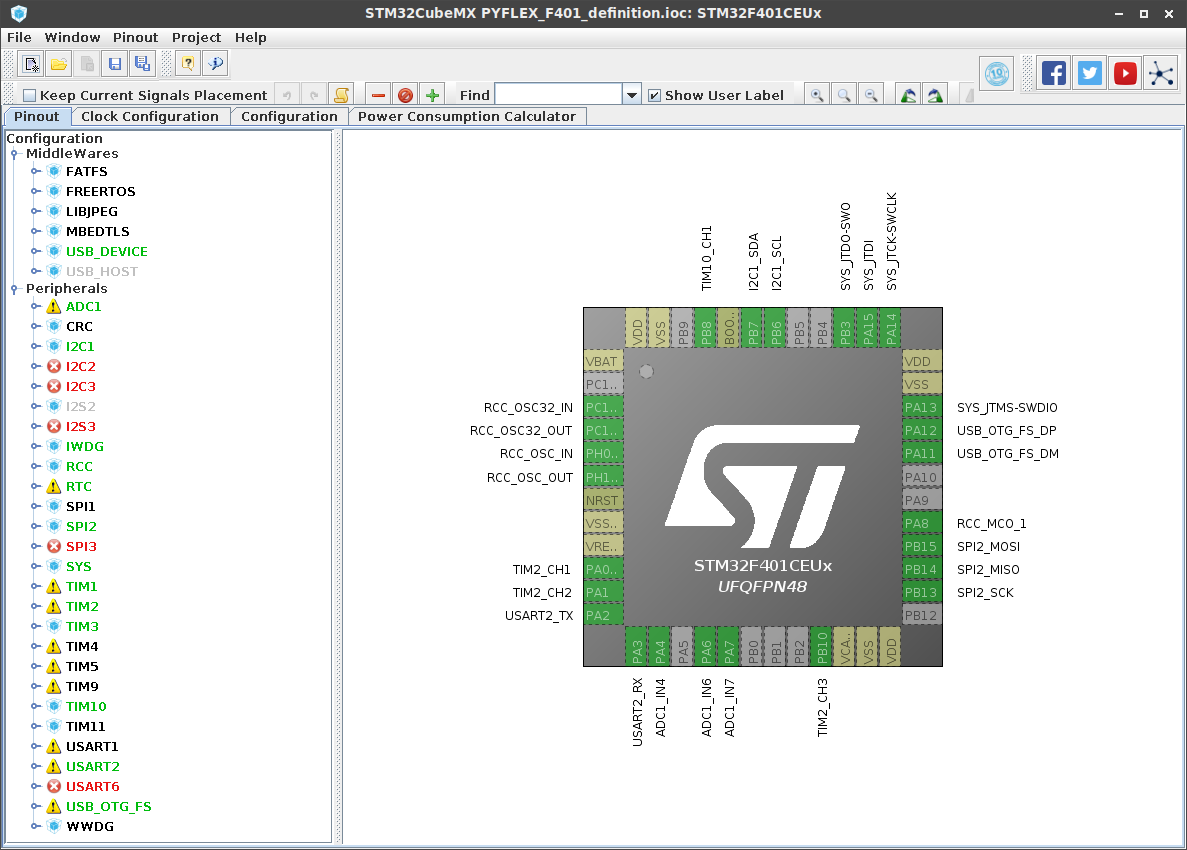
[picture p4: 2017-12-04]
hardware_schematics_layouts/STM32cubemx-pins.png

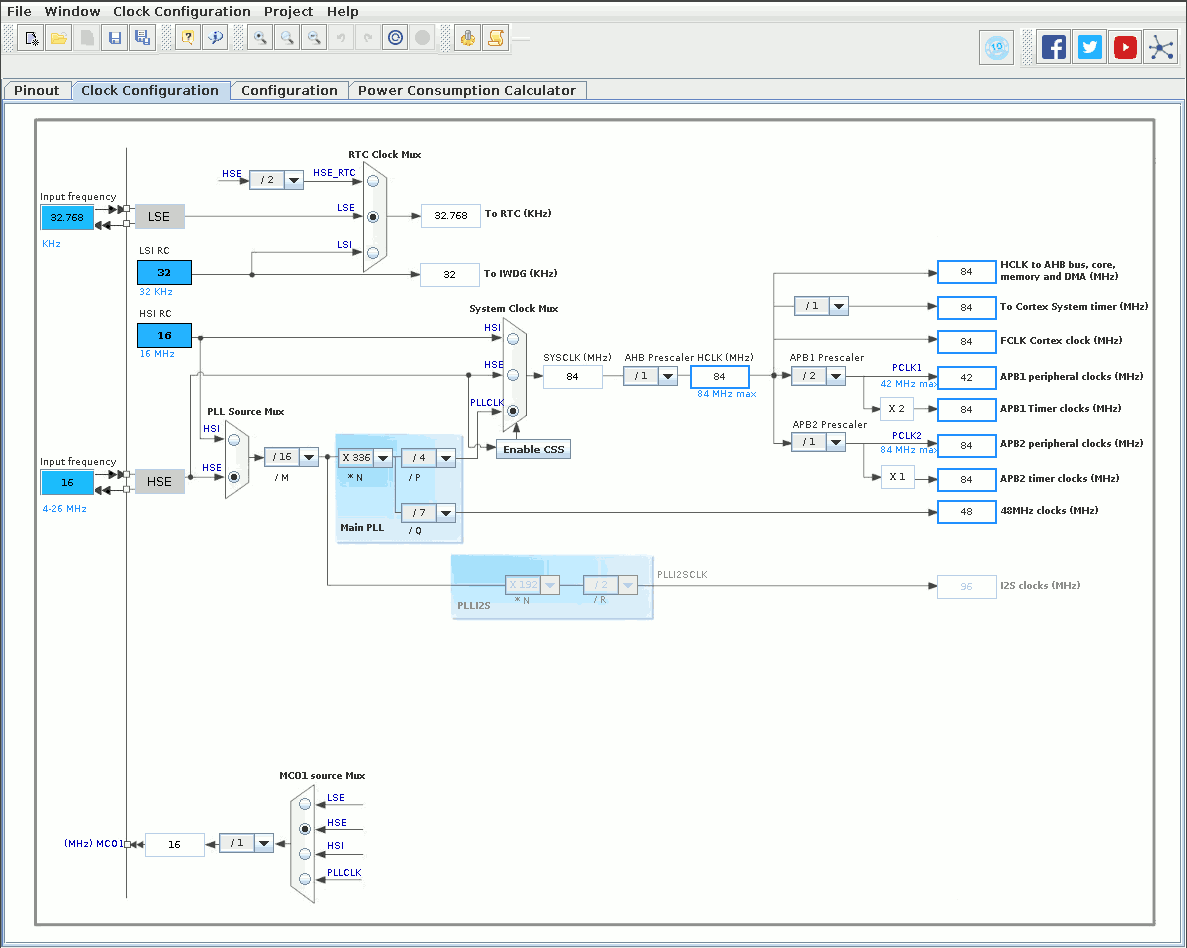
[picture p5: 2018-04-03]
hardware_schematics_layouts/STM32cubemx-clocks.png

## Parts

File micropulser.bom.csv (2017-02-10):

.START
..device | value | footprint | quantity | refdes
CAPACITOR | 20 pF | unknown | 2 | C6 C7
CAPACITOR | 4.7 uF | unknown | 1 | C2
CAPACITOR | 4.7nF | unknown | 1 | C19
CAPACITOR | 9 pF | unknown | 2 | C8 C9
CAPACITOR | unknown | unknown | 4 | C1 C3 C4 C5
COIL | unknown | unknown | 1 | L3
CRYSTAL | 12MHz | unknown | 1 | X1
CRYSTAL | unknown | unknown | 1 | X2
RESISTOR | 100K | unknown | 1 | R5
RESISTOR | 22 | unknown | 2 | R6 R7
stm32f401cb | unknown | stm32f401cb | 1 | U1
SWITCH_PUSHBUTTON_NO | unknown | unknown | 1 | S1
unknown | unknown | unknown | 1 | U?
USB | unknown | USB_mini_TYPE-B_SMT | 1 | J?
zif_connector | unknown | ffc_zif_20.fp | 1 | J1
.END

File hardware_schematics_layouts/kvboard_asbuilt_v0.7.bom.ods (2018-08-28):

 |  | kvboard_asbuilt_v0.7.bom.osd
device | value | footprint | qty | refdes
36-110 | conn | cuvette_cont_notch_L.lht | 1 | J3
36-110 | conn | cuvette_cont_notch_R.lht | 1 | J2
472-3KV | 4.7nF | disk_cap_5mm_flat.lht | 2 | C1 C3
472-3KV | 4.7nF | disk_cap_5mm_flat_flip.lht | 2 | C2 C4
B5819WS | .9V .5W | SOD-323N.lht | 2 | D5 D6
BC857BDW1T1 | BJT dual | SOT363M.lht | 1 | U3
CL10B104MB8NNNC | 1 nF | CAPC1608N.lht | 2 | C50 C60
CL31A106MBHNNNE | 10 uF | CAPC3216N.lht | 2 | C51 C61
CS1-HVT-EPC19-04 | xfmr | TXFMR_EPC19.lht | 1 | T1
CS25N06B4 | NFET | DPAK1.lht | 2 | Q50 Q60
FC5030-06 | conn | ffc_zif_06_1.25.lht | 1 | J4
FC5030-20 | conn | ffc_zif_20_1.25.lht | 1 | J1
MUN5232DW1T1G | BRT NPN dual | SOT363M.lht | 1 | U4
R3000 | 3KV | diode_10mm.fp | 4 | D1 D2 D8 D10
R_1.80k_1%_1608 | 1.80k | RESC1608N.lht | 2 | R34 R35
R_133_1%_2013 | 133 | RESC2013N.lht | 2 | R27 R96
R_200_1%_2013 | 200 | RESC2013N.lht | 4 | R50 R51 R60 R61
R_22.0_1%_1608 | 22 | RESC1608N.lht | 8 | R43 R44 R90 R91 R92 R93 R94 R95
R_220_1%_1608 | 220 | RESC1608N.lht | 4 | R32 R33 R45 R46
R_3.30k_1%_1608 | 3.30k | RESC1608N.lht | 2 | R36 R37
R_22.0k_1%_1608 | 22.0K | RESC1608N.lht | 2 | R38 R39
R_9.10k_1%_1608 | 9.10K | RESC1608N.lht | 2 | R30 R31
RC1206FR-07475KL | 475K | RESC3216N.lht | 8 | R1 R2 R3 R4 R5 R6 R7 R8
Res_2.20k_1%_1608 | 2.20k | RESC1608N.lht | 2 | R41 R42
Res_680_1%_1608 | 680 | RESC1608N.lht | 2 | R55 R65
S1Y | 2KV | DIOM_SMAFN.lht | 4 | D3 D4 D7 D9
STPS2L25U | .375V 2A | SMB_N.lht | 2 | D50 D60
TZC3Z060A110 | 6pF | CAP_VAR3040N.lht | 1 | C16
TZC3Z300A110 | 30pF | CAP_VAR3040N.lht | 1 | C15
VZH471M1ETR-1010 | 470 uF | CAPAE10X10.lht | 6 | C52 C53 C54 C62 C63 C64
.END

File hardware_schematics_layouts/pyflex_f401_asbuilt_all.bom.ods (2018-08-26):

 |  | pyflex_f401 v0.7 assembly
device | value | footprint | quan | refdes
06033C104KAT2A | 0.1 uF | CAPC1608N.lht | 9 | C4 C6 C7 C8 C12 C23 C102 C103 C104
06033C104KAT2A | 0.1 uF 25V | CAPC1608N.lht | 1 | C61
AO3407A | PFET | SOT23-3N.lht | 6 | Q1 Q2 Q4 Q5 Q7 Q8
B5819WS | 9Apulse .5W | SOD-323N.lht | 1 | D31
BC807-40L | BJT PNP | SOT323N.lht | 1 | Q31
BC817W | BJT NPN | SOT323N.lht | 3 | Q3 Q6 Q9
BC857BDW1T1 | unknown | SOT363M.lht | 1 | U8
BXIDM03-05-01-P001-L/T-P-F | conn | hdr_mini_1.25_2x5.lht | 1 | JC
CC1206KFX5R8BB106 | 10 uF | CAPC3216N.lht | 1 | C31
CL10A105KA5LNNC | 1 uF | CAPC1608N.lht | 6 | C5 C17 C18 C21 C22 C32
CL10A475MO8NNNC | 4.7uF | CAPC1608N.lht | 5 | C9 C10 C11 C62 C101
CL21B105KBFNFNE | 3.3pF | CAPC1608N.lht | 1 | C33
ELMCUSB5SMT_WP | conn | USB_AB_micro_4leg_WR.lht | 2 | JD JUSB
ESD11B5.0ST5G | 5.0V | DIOM_DSN2.lht | 4 | VS1 VS2 VS3 VS4
JUMPER_SOLDER | layout-shape | jump-solder1.lht | 3 | J21 J31 J32
LED 0805 | GRN LED | DIOC2013N.lht | 1 | D12
LED-0805 | GRN LED | DIOC2013N.lht | 1 | D11
LED-0805 | YEL LED | DIOC2013N.lht | 1 | D13
MLCC_12pF_50V | 12 pF | CAPC1608N.lht | 2 | C13 C14
MLCC_7pF_50V | 7 pF | CAPC1608N.lht | 2 | C15 C16
MLZ2012N100LT000 | 10uH | INDC2013N.lht | 1 | L10
MUN5232DW1T1G | BRT NPN | SOT363M.lht | 1 | U5
NRH2410T100MN | 10 uH | INDC2424N.lht | 1 | L31
NRS2012T4R7MGJ | 4.7 uH | INDC2020N.lht | 1 | L61
Q13FC1350000200 | 32.78k | XTAL_3215.lht | 1 | X2
Q24FA20H0012200 | 16.0M | XTAL_FA20H.lht | 1 | X1
R_0R22_1%_1608 | 0.22 | RESC1608N.lht | 1 | R65
R_1.0k_1%_1608 | 1.0k | RESC1608N.lht | 2 | R20 R21
R_1.80k_1%_1608 | 1.80k | RESC1608N.lht | 9 | R9 R64 R104 R106 R109 R110 R118 R122 R129
R_1.8k_1%_1608 | 1.80K | RESC1608N.lht | 2 | R37 R39
R_133_1%_2013 | 133 | RESC2013N.lht | 2 | R17 R18
R_180K_1%_1608 | 180k | RESC1608N.lht | 9 | R14 R32 R35 R101 R102 R120 R121 R126 R127
R_1M0_1%_1608 | 1M0 | RESC1608N.lht | 1 | R31
R_1M3_1%_1608 | 1M3 | RESC1608N.lht | 1 | R36
R_22.0_1%_1608 | 22 | RESC1608N.lht | 4 | R6 R7 R8 R119
R_62k_1%_1608 | 62.0k | RESC1608N.lht | 1 | R63
R_7.50k_1%_1608 | 7.50k | RESC1608N.lht | 13 | R33 R34 R38 R103 R105 R108 R111 R112 R113 R114 R115 R123 R128
Res thick 033R 1% 1/8W 2013 | 33 | RESC2013N.lht | 1 | R124
SSM3K15AFS | NFET | SOT416N.lht | 1 | Q32
STM32F401CE | IC | UFQFPN48-F401CE.lht | 1 | U1
SWITCH_PB_NO_4MM | N.O. | SWITCH_4mm.lht | 3 | SW11 SW22 SW23
terminal-layout | layout | term-pad-3x4.lht | 6 | JB6 JB7 JE JF JG JH
TLV70231DBVR | 3V1 | SOT23-5N.lht | 1 | U2
TP5000 | IC | QFN16_4040N.lht | 1 | U6
TPS61040DBVR | IC | SOT23-5.lht | 1 | U3
zif_connector | conn | ffc_zif_20_1.25.lht | 2 | JA JB

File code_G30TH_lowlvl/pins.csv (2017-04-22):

X1 | PA0
X2 | PA1
X3 | PA2
X4 | PA3
X5 | PA4
X6 | PA5
X7 | PA6
X8 | PA7
X9 | PB6
X10 | PB7
X11 | PC4
X12 | PC5
X13 | Reset
X14 | GND
X15 | 3.3V
X16 | VIN
X17 | PB3
X18 | PC13
X19 | PC0
X20 | PC1
X21 | PC2
X22 | PC3
X23 | A3.3V
X24 | AGND
Y1 | PC6
Y2 | PC7
Y3 | PB8
Y4 | PB9
Y5 | PB12
Y6 | PB13
Y7 | PB14
Y8 | PB15
Y9 | PB10
Y10 | PB11
Y11 | PB0
Y12 | PB1
Y13 | Reset
Y14 | GND
Y15 | 3.3V
Y16 | VIN
SW | PB3
LED_RED | PA13
LED_GREEN | PA14
LED_YELLOW | PA15
LED_BLUE | PB4
MMA_INT | PB2
MMA_AVDD | PB5
SD_D0 | PC8
SD_D1 | PC9
SD_D2 | PC10
SD_D3 | PC11
SD_CMD | PD2
SD_CK | PC12
SD | PA8
SD_SW | PA8
USB_VBUS | PA9
USB_ID | PA10
USB_DM | PA11
USB_DP | PA12

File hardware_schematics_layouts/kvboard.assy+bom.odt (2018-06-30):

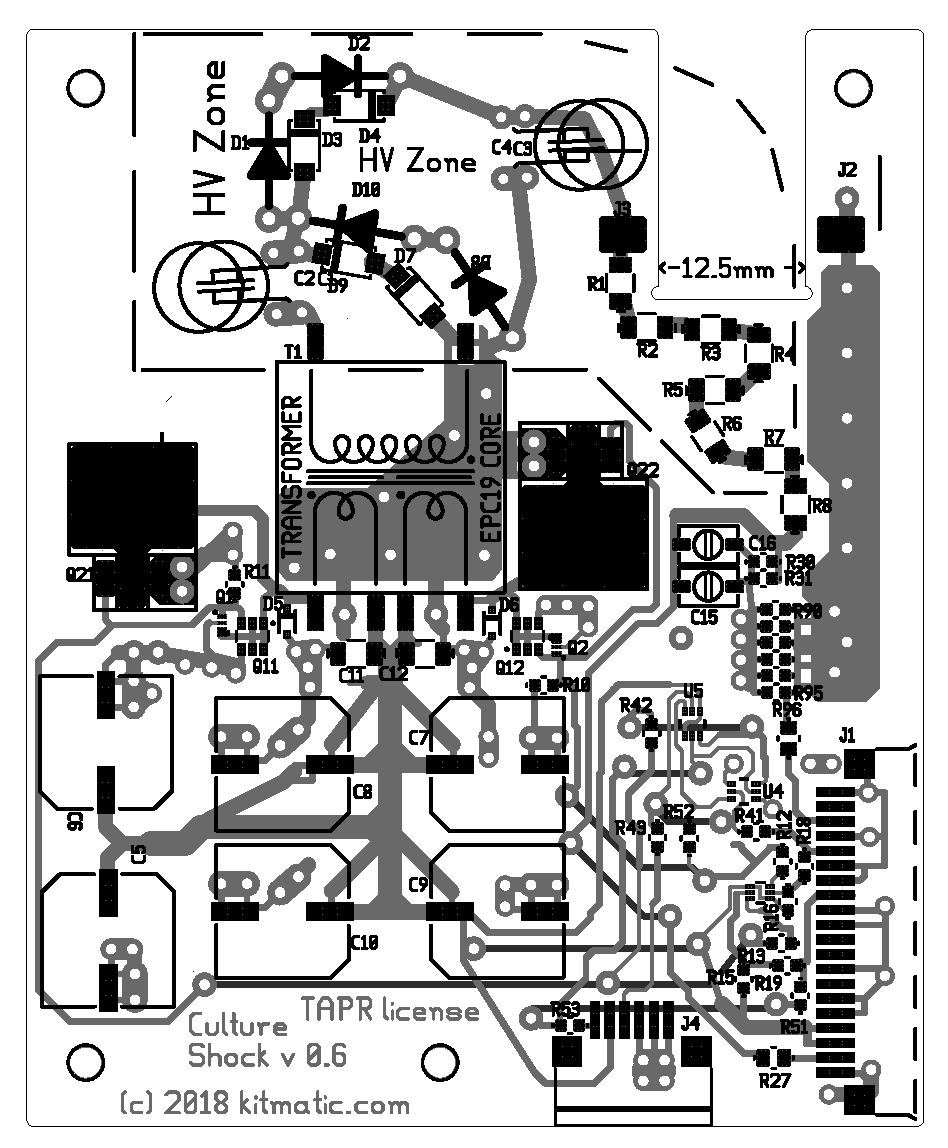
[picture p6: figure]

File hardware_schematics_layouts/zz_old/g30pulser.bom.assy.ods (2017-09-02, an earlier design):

device | value | footprint | quantity | refdes
AP2120N-TRG1 | 3.3 | SOT23-123.fp | 1 | U1
BSD840N | unknown | SOT363-most.fp | 1 | U2
ffc_zif_20 | connect | ffc_zif_20.fp | 1 | J1
header20single | na | header20single.fp | 1 | J2
MF-CAP-0603-0.1uF | 0.1 uF | chip_1608_0603_N.fp | 1 | C1
MF-CAP-0603-1uF | 1 uF | chip_1608_0603_N.fp | 2 | C2 C3
MF-RES-0805-220 | 220 | chip_2012_0805_N.fp | 7 | R1 R2 R3 R5 R6 R8 R9
MF-RES-0805-220 | 4.75K | chip_2012_0805_N.fp | 1 | R11
MF-RES-0805-220 | 4.75k | chip_2012_0805_N.fp | 2 | R4 R7
SWITCH_PUSH_NO | na | push_b_6mm.fp | 2 | S1 S2

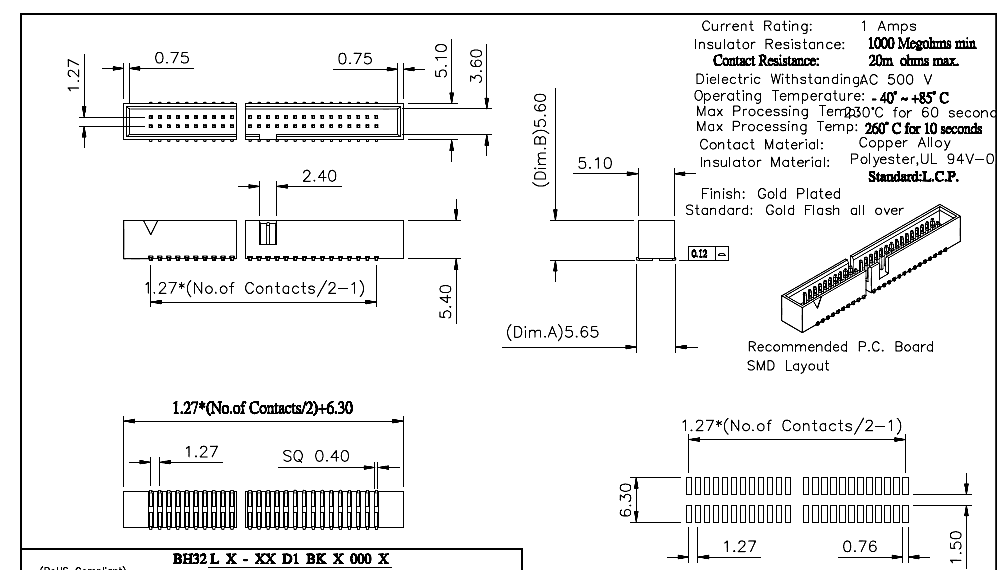
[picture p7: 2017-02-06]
parts/jvtcn_1.27_box_header.gif

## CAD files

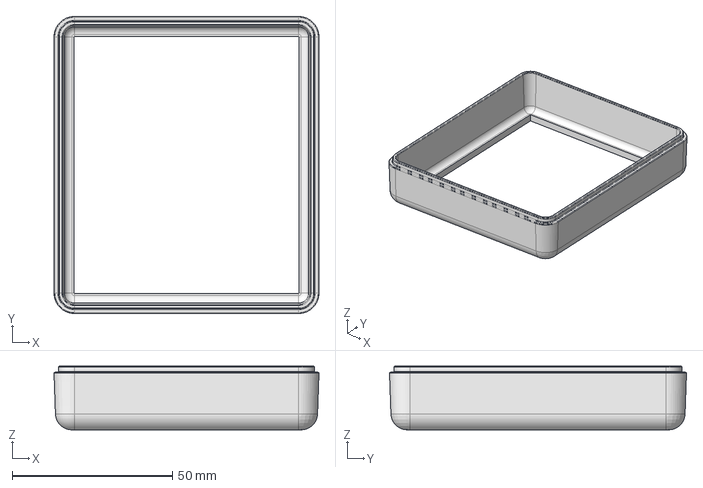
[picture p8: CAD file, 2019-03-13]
enclosure/broken/cs-enc-spread-driven-11broken-offsets.fcstd
82.8 x 92.8 x 19.9 mm

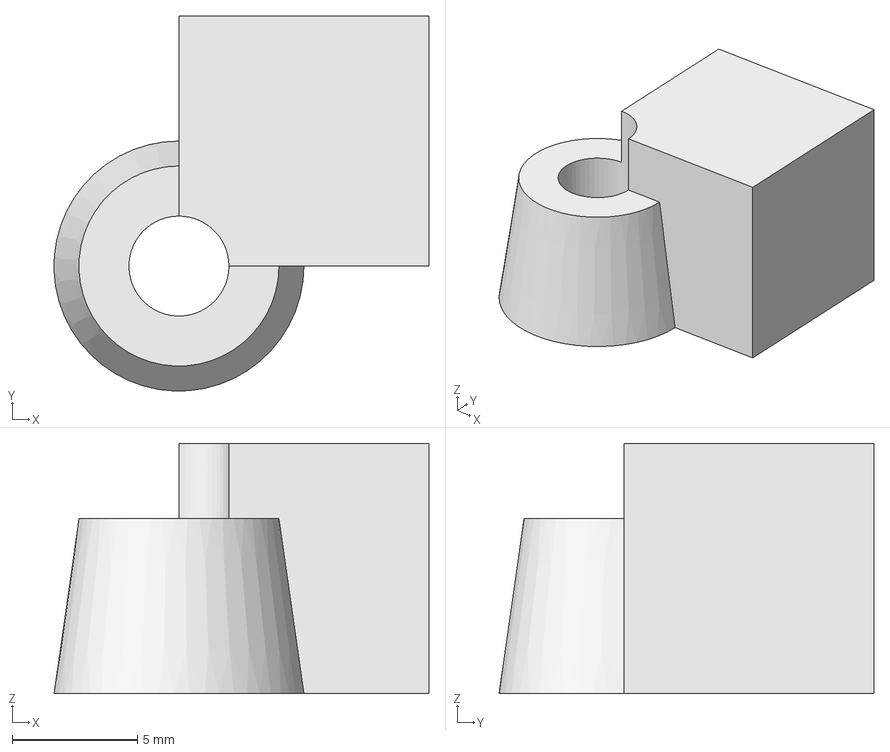
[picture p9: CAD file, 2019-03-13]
enclosure/subtractive-shape-save-test2.FCStd
15.0 x 15.0 x 10.0 mm

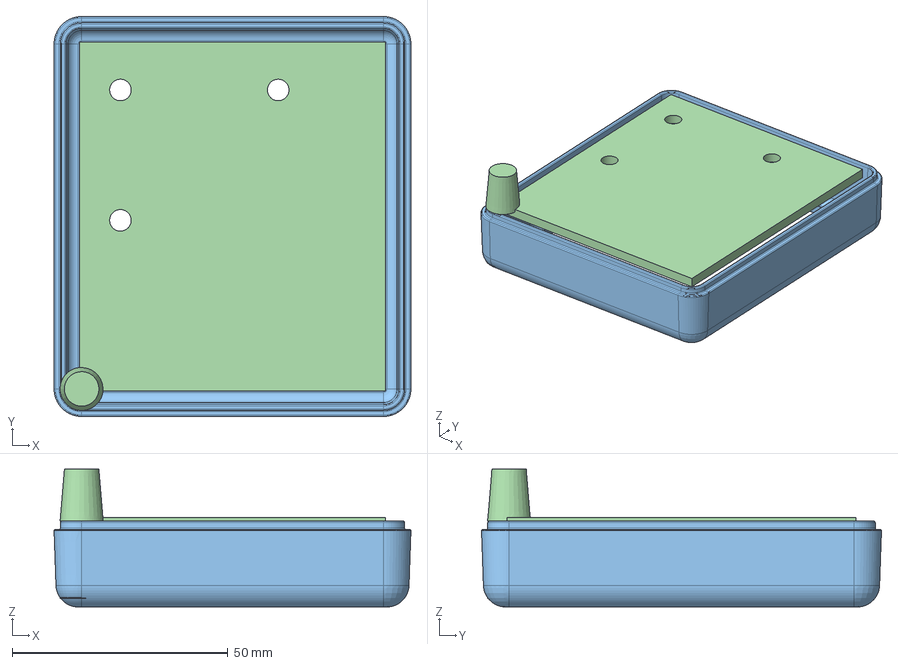
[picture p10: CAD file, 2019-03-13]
enclosure/broken/cs-enc-spread-driven-09c4broken.fcstd
82.8 x 92.8 x 32.0 mm
cs-enc-back-sweep
cs-enc-back-floor-n-bosses
AdditivePipe

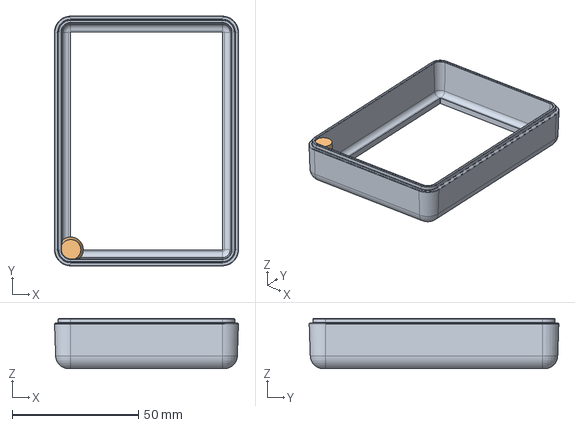
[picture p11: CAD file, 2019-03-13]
enclosure/cs-enc-15d.fcstd
72.8 x 98.8 x 19.9 mm
cs-enc-back-sweep
cs-enc-back-floor-n-bosses

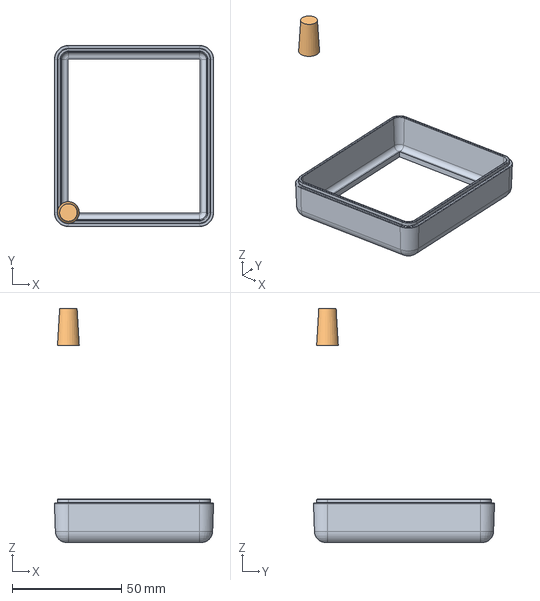
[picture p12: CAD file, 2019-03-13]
enclosure/broken/cs-enc-spread-driven-13broken.fcstd
72.8 x 82.8 x 107.0 mm
cs-enc-back-sweep
cs-enc-back-floor-n-bosses

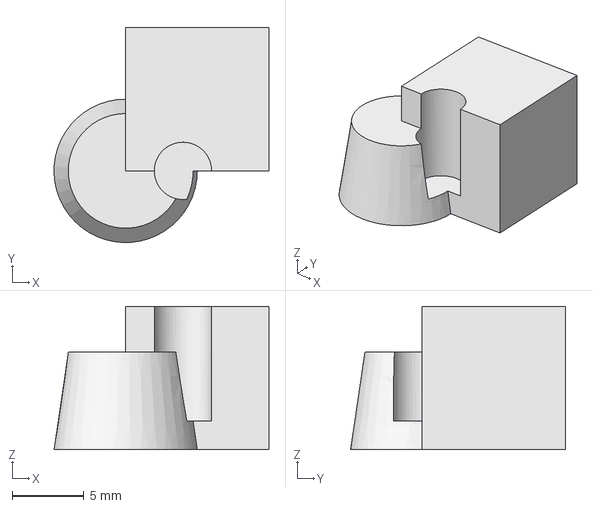
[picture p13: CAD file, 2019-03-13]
enclosure/subtractive-shape-save-test3.FCStd
15.0 x 15.0 x 10.0 mm

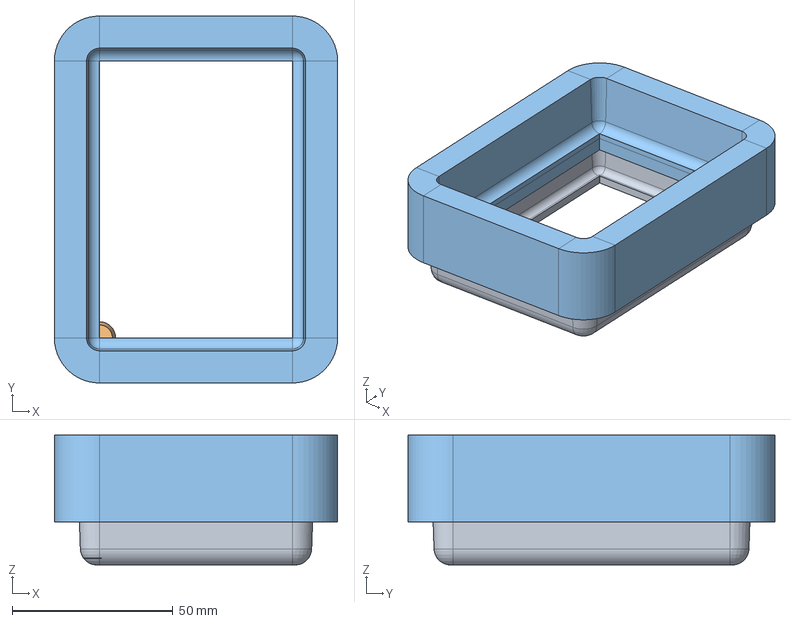
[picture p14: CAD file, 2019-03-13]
enclosure/cs-enc-15e.fcstd
88.1 x 114.1 x 40.4 mm
cs-enc-back-sweep
cs-enc-back-floor-n-bosses
cs-enc-bosses-subtract

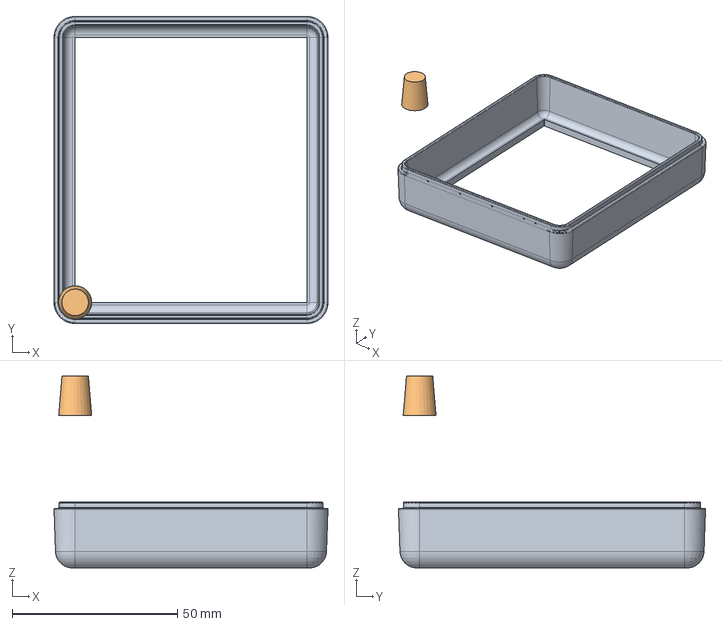
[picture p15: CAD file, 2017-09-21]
enclosure/broken/cs-enc-spread-driven-10broken.fcstd
82.8 x 92.8 x 58.0 mm
cs-enc-back-sweep
cs-enc-back-floor-n-bosses

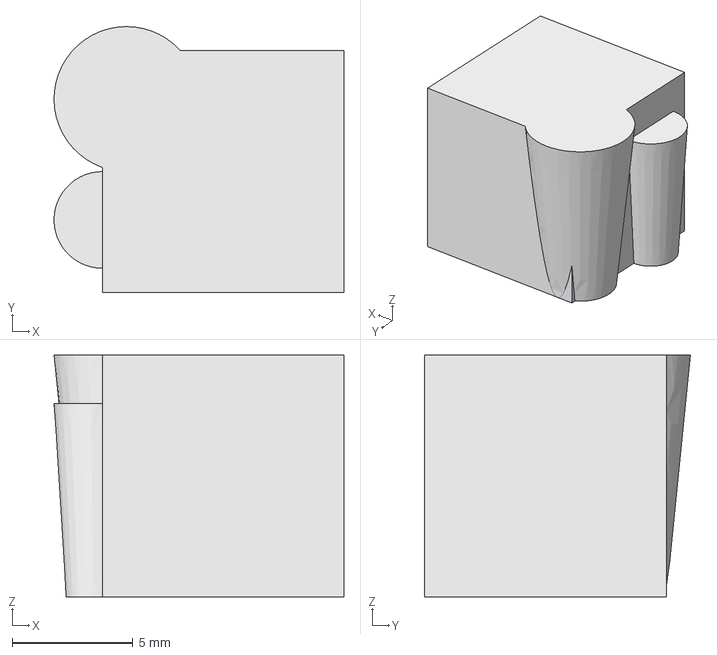
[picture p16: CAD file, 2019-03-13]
enclosure/subtractive-shape-save-test3b.FCStd
12.0 x 11.0 x 10.0 mm

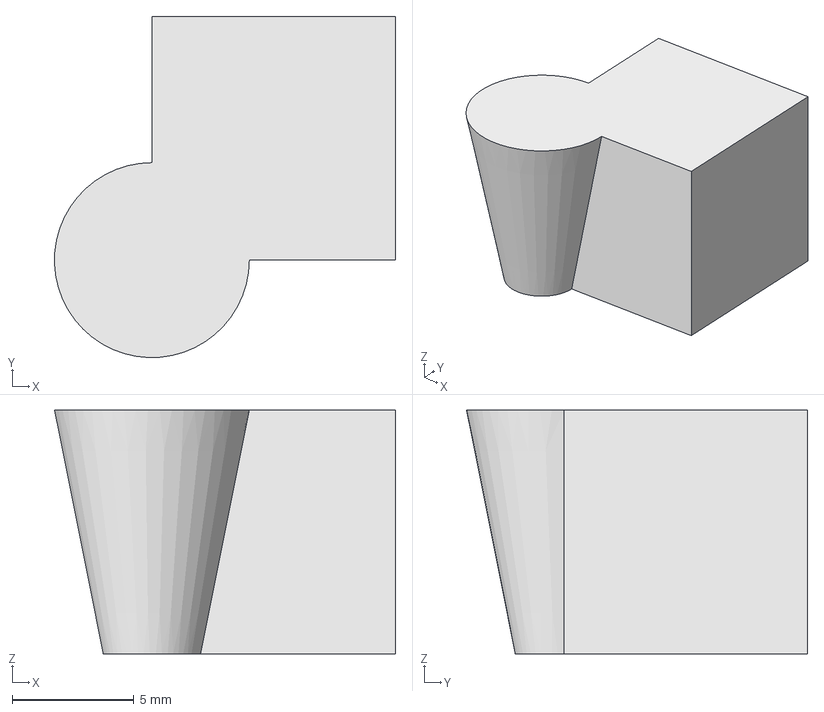
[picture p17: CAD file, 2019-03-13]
enclosure/subtractive-shape-save-test2b.FCStd
14.0 x 14.0 x 10.0 mm

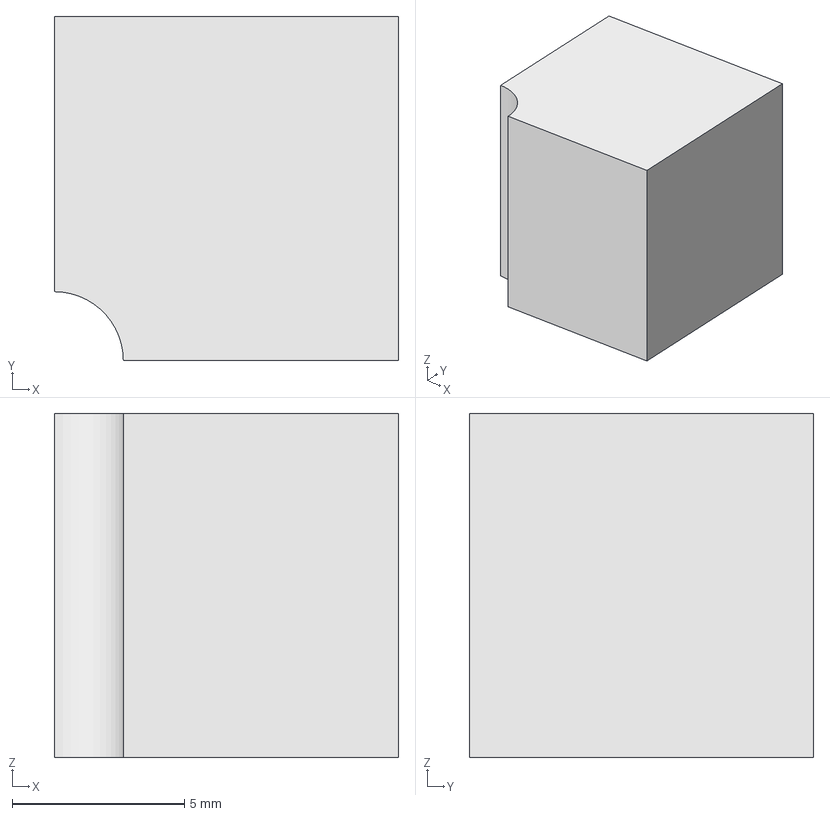
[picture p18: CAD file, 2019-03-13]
enclosure/subtractive-shape-save-test.FCStd
10.0 x 10.0 x 10.0 mm

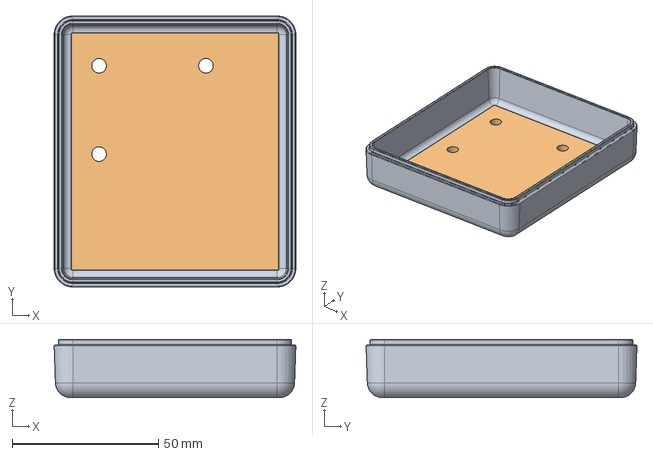
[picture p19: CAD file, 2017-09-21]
enclosure/cs-enc-spread-driven-part-02.fcstd
82.8 x 92.8 x 19.9 mm

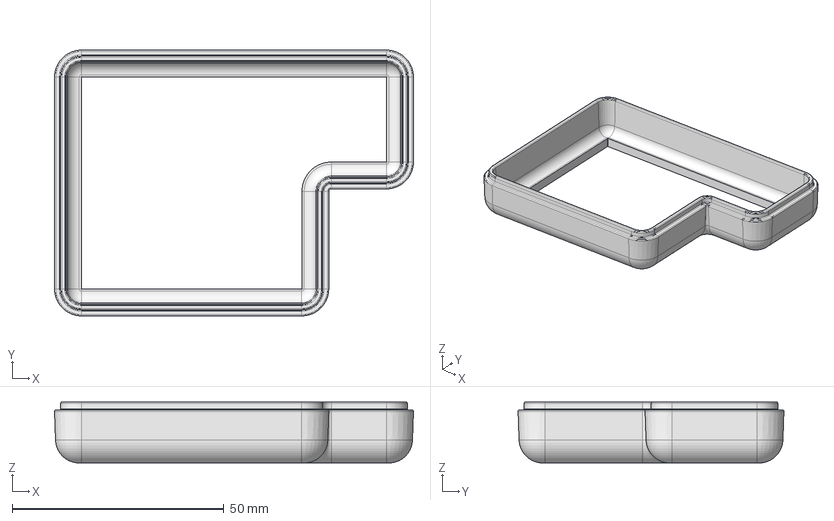
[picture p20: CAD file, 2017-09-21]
enclosure/cs-enc-back-swept-4.9mm-1.fcstd
84.8 x 62.8 x 14.4 mm

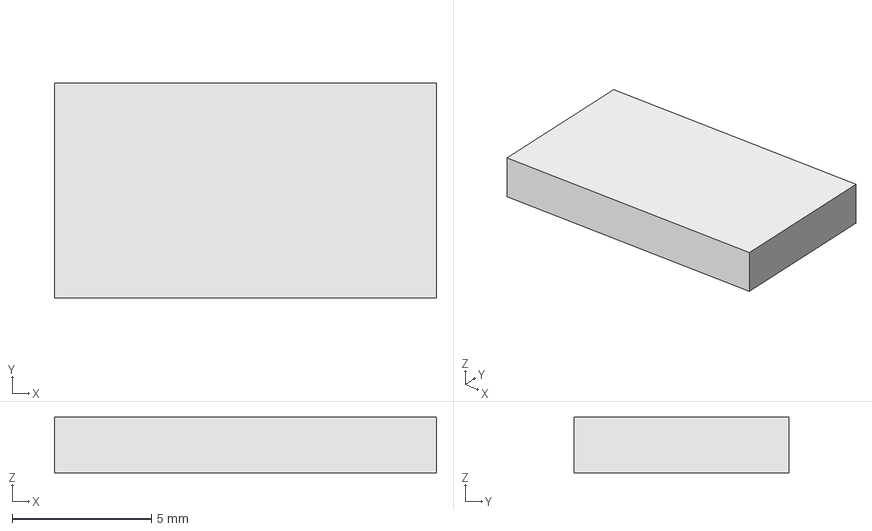
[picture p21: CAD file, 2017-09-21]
enclosure/simple-box-test-highlighting2.fcstd
13.7 x 7.73 x 2.00 mm

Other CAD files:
enclosure/broken/cs-enc-spread-driven-09broken.fcstd
enclosure/cs-enc-15c.fcstd
enclosure/cs-enc-spread-driven-bodypart-01.fcstd
enclosure/simple-box-test-highlighting.fcstd
enclosure/cs-enc-back-bathtub-drafted.fcstd
enclosure/cs-enc-back-perim.fcstd
enclosure/cs-enc-back-sketch.fcstd
enclosure/cs-enc-front-edgesweep-1.step
enclosure/cs-enc-shapebinder-1.fcstd
enclosure/cs-enc-spread-driven-01.fcstd
enclosure/cs-enc-spread-driven-02.fcstd
enclosure/cs-enc-spread-driven-03.fcstd
enclosure/cs-enc-spread-driven-04.fcstd
enclosure/cs-enc-spread-driven-05.fcstd
enclosure/cs-enc-spread-driven-07.fcstd
enclosure/cs-enc-spread-driven-09.fcstd
enclosure/cs-enc-spread-driven-part-01.fcstd
enclosure/cut-example.fcstd
enclosure/old/FC017_Body_with_Draft_Polygon.fcstd
enclosure/old/Fillet--pipe-b-spline.fcstd
enclosure/old/cs-enc-back-bathtub-drafted.fcstd
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

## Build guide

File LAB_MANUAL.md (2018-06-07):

Culture_Shock Lab Manual - Table of Contents
=================

   * [Growth media preparation](#growth-media-preparation)
      * [Background](#background)
      * [Sources](#sources)
         * [LB broth](#lb-broth)
         * [LB agar](#lb-agar)
      * [Protocols](#protocols)
         * [LB Broth](#lb-broth-1)
         * [LB Agar Plates](#lb-agar-plates)
         * [Weighing powder step-by-step](#weighing-powder-step-by-step)
         * [Sterilization of culture media](#sterilization-of-culture-media)
            * [Wet Sterilization](#wet-sterilization)
               * [Step-by-step](#step-by-step)
         * [Dry Sterilization](#dry-sterilization)
         * [Adding antibiotics or other heat-sensitive chemicals to agar or broth media](#adding-antibiotics-or-other-heat-sensitive-chemicals-to-agar-or-broth-media)
   * [Cell Subculture basics](#cell-subculture-basics)
   * [Subculture with broth](#subculture-with-broth)
   * [Subculture with agar](#subculture-with-agar)
      * [if original bacterial culture is from a solid/firm culture source](#if-original-bacterial-culture-is-from-a-solidfirm-culture-source)
      * [if original bacterial culture is from a liquid culture source](#if-original-bacterial-culture-is-from-a-liquid-culture-source)
   * [Transformation](#transformation)
      * [Chemical Transformation (CaCl<sub>2</sub>)](#chemical-transformation-cacl2)
      * [Electroporation (culture_shock method!)](#electroporation-culture_shock-method)
   * [Overall steps (E.coli subculture, plasmid extraction, plasmid electroporation)](#overall-steps-ecoli-subculture-plasmid-extraction-plasmid-electroporation)
      * [Day 1](#day-1)
      * [Day 2](#day-2)
      * [Day 3](#day-3)
      * [Day 3.5](#day-35)
      * [Day 4](#day-4)

# Growth media preparation
## Background
Sterilization of nutrients and energy sources, and to prevent competition with any organisms we wish to grow, we aim to kill off all other organisms.

It has been found that E.Coli prefers a salty broth with protein and nutrients, usually made from:
* tryptone
  * casein protein from milk that has been partially digested into shorter fragments using the protease enzyme Trypsin, which in found for instance in the Human intestine
* NaCl
  * sodium chloride, for osmotic balance
* yeast extract
  * vitamins; minerals; trace elements like N, S, and Mg; a plethora of other organic compounds helpful for bacterial growth

This broth may be stabilized into a gel using agar, a polysaccharide extracted from algae which is indigestible for many microbes. Gelatin is not preferred as it is made of protein, which is quick to be digested by growing organisms, turning soupy. 

## Sources
### LB broth
* [from The-ODIN](https://www.the-odin.com/lb-powdered-media/)
  * Lennox recipe, which has 5g/L NaCl salt:
    * 10g/L Tryptone
    * 5 g/L Yeast Extract
    * 5 g/L NaCl

### LB agar
* [from The-ODIN](https://www.the-odin.com/lb-agar/)
  * Miller recipe, which has 10g/L NaCl salt:
    * 5 g/L Tryptone
    * 5 g/L Yeast Extract
    * 10g/L NaCl
    * 15g/L Agar

## Protocols

### LB Broth
* mix 20 g __LB broth powder mix__ with 1 Liter of distilled water

### LB Agar Plates
* mix 40 g __LB agar powder mix__ with 1 Liter of distilled water, then autoclave. 1 Liter makes ~35-40 Plates.
  * read The-ODIN's instructions [here](https://docs.google.com/document/d/1UcbshGXeTEyNg-4ZxiJDeOM8r6mN5CZDreM5c7n6bzE/edit)

### Weighing powder step-by-step
* obtain glass container which is heat safe (canning jar, erlenmeyer flask)
* put on a pair of nitrile gloves
* place weigh boat on scale
* turn on scale, wait for it to read __0.0__
* hold powder bottle in one hand
* to open, unscrew the lid with your other hand
  * I don't recommend putting the lid down, I would continue to hold it
* tap the bottle to slowly shake out the powder into the weigh boat
* tilt the bottle less and less, as you approach 20.0 grams on the scale display
* close the bottle
* dump the contents of the weigh boat into a glass container (canning jar, erlenmeyer flask)
* add distilled water 
  * tap water will likely suffice, but may be more variable from day-to-day than bottled distilled water
* finish with "Wet Sterilization" instructions

### Sterilization of culture media
Industrial, commercial, academic, and medical professions use a device called an autoclave to sterilize growth media and other things like empty containers, cloths, and metal tools. Autoclaves are basically automated pressure-cookers.

#### Wet Sterilization
* heat is transferred via exposure to steam
* requires 121 °C (250 °F) for 15 to 30 minutes, depending on liquid volume and container geometry.
  * pressure cookers working at 15 PSI (at sea level) will produce 121 °C

##### Step-by-step
* obtain container with agar or broth mixture in it
* cover the container opening with a square piece of aluminum foil
* swirl gently to mix, don't worry if it doesn't all dissolve, the heat during sterilzation will take care of that

__NOTE__: do not fill any container more than 50% full, it risks overflowing during sterilization due to bubbles and/or froth
* add water to 

### Dry Sterilization
* uses an oven and heats through convection and radiation
* requires 160 °C (320 °F) for 2 hours or 170 °C (340 °F) for 1 hour.
  * use an oven bag, like those sold by the Reynolds company for baking turkeys inside of (remember the product "Shake 'n Bake"?)
* Instruments should be dry before sterilization since water will interfere with the process.

### Adding antibiotics or other heat-sensitive chemicals to agar or broth media
Some chemicals are very heat-sensitive and need to be added after sterilization, when the media container has cooled to the (per-chemical) specified temperature.

# Cell Subculture basics
* Once you have broth media, you can add bacteria to it with a sterile stick or metal/plastic innoculation loop.
* Sometimes you don't trust the source of the bacteria, and want to make sure there isn't contamination from other species.
* For these situations you will use a planar growth media, otherwise known as agar gel media (petri dishes, or 'plates').
* By reducing the available growth surface to essentially a solid 2D plane, you may see segregated and distinct growth patterns when multiple species are growing at once.
* This also enables you to remove a portion of these 'colonies' which are pure-appearing, and repeat this subculture growth process on a fresh agar plate, to purify mixed cultures over multiple selection steps.

# Subculture with broth
* if original bacterial culture is from a solid/firm culture source
  * Using a sterile stick/toothpick/innoculation-loop, retrieve a sample from a single colony (or more if desired)
* if original bacterial culture is from a liquid culture source
  * Using a pipette, aspirate (suck) 0.1 to 1.0 mL (usually, depends on the specific experiment)
* Open the media jar in a clean-air (HEPA filtered) or still-air
* place the stick/toothpick/innoculation-loop into the broth, flick/swish/rotate
  * __be careful not to touch the container insides__ with your glove
* close the jar
* label the jar with a sharpie marker (you may use a piece of masking tape to write on)
* place in incubator

# Subculture with agar
## if original bacterial culture is from a solid/firm culture source
* Using a sterile stick or toothpick, retrieve a sample from a single colony (or more if desired)
* Open the petri dish
* place the stick onto the surface of the agar
* gently drag the stick across the surface, from one side to the other
* continue in a zig-zag fashion down the remaining surface
  * if your drag lines do not cross, this will effectively dilute the number of bacteria (colony formation units, CFUs) along the entire streak, with the most bacteria being concentrated at the beginning and least at the end.
* label the petri dish with a sharpie marker (you may use a piece of masking tape to write on)
* place in incubator

## if original bacterial culture is from a liquid culture source
* Using a pipette, aspirate (suck) 0.1 mL (usually, maybe less if this is determined to be too wet)
* dispense liquid culture on the surface of the agar
* if you have a cell spreader (L shaped piece of metal or glass)
  * gently drag and push the spreader back and forth across the surface of the agar
  * rotate the petri dish with your other hand, as you continue to push and pull the cell spreader
  * continue until you have made several complete rotations of the petri dish while spreading
* if you have sterile glass beads
  * place the beads into the petri dish, cover the dish
  * roll the beads around to attempt to evenly distribute the liquid across the agar surface
  * open the dish, pour out the beads into a container
* label the petri dish with a sharpie marker (you may use a piece of masking tape to write on)
* place the petri dish in incubator

# Transformation
## Chemical Transformation (CaCl<sub>2</sub>)
Read The-ODIN's protocol for transforming a plasmid into E.Coli [here](https://docs.google.com/document/d/1fGiyux6qxCHHIzhYNCZx23z8v785IhyUg_CP57odpv4/edit)
* requires extra chemicals (CaCl<sub>2</sub>)
* requires 30 minute cool-down
* requires 30 second heat-shock

## Electroporation ([Using Culture Shock](USING_CULTURE_SHOCK.md "USING_CULTURE_SHOCK.md"))
* obtain 1mL of log-phase E.Coli broth culture (log-phase occurs after about 4-6-hours in 37° shaker incubator)
<div>
<br><sub>from M.Komorniczak at wikimedia</sub></div>

* determine how many RPMs you need to centrifuge your cells at, based on the radius of your centrifuge rotor
  * We are going 'softer' than the common rule of thumb: __aiming to achieve 2000 [RCF](https://en.wikipedia.org/wiki/Centrifuge#Mathematical_description) ("g"s)__
    * rule of thumb: 180-250 rcf, 5 mins for mammalian cells; 4000-6000 rcf, 5-10 mins for bacteria
    * [Use this handy RCF (g-forces) to RPM calculator](http://insilico.ehu.es/mini_tools/rcf_rpm.php), you just need to measure your rotor in __mm__
* repeat the following (3) times
  * centrifuge the cell solution at the calculated RPM for 3 minutes
  * discard the liquid, allowing the "cell pellet" to remain
  * add 1 mL distilled H<sub>2</sub>O
  * resuspend by pulsing with vortexer
* resuspend once more in H<sub>2</sub>O, either 75 µL or 200µL
  * for 2 mm gap electroporation cuvette, pipette 200 µl (completely full)
  * for 1 mm gap VWR electroporation cuvette, pipette 75 µl  (completely full)

* Transfer 1 pg–100 ng of plasmid DNA (1–5 µl) to cells and mix without vortexing.
  
Electroporation at low temperature (0-4 °C) seems to work best according to evidence, and efficiencies may drop ~100-fold at room temperature
* for best results, pre-chill the cuvette and cell suspension on ice for 1 to 2 minutes

* transfer cell solution to electroporation cuvette
  * for 2 mm gap electroporation cuvette, maximum volume during pulse is 400 µl
  * for 1 mm gap VWR electroporation cuvette,  preferred volume during pulse is 75 µl tolerance 10% over, zero under.

## Pulse with E.coli settings ([Using Culture Shock](USING_CULTURE_SHOCK.md "USING_CULTURE_SHOCK.md"))
* immediately add 1mL LB broth (or SOC broth for better efficiency)
* incubate for 30 to 60 mins
  * if ampicillin resistance gene was transformed 30 mins
  * if kanamycin, 60 mins
* transfer to agar plates, using [cell-spreader technique](#if-original-bacterial-culture-is-from-a-liquid-culture-source)

# Overall steps (E.coli subculture, plasmid extraction, plasmid electroporation)
## Day 1
* Prepare agar, agar+antibiotics, broth media
  * sterilize, let cool to antibiotic-safe temperature
  * add antibiotic to one of the two agar containers
    * write label, noting it has antibiotics
  * add antibiotic to one of the two broth containers
    * write label, noting it has antibiotics
  * portion agar into petri dishes

* Subculture cells in agar to ensure purity
  * successive agar sub-culturing may be required if contamination is present
    * E.coli __with plasmid__ go on __antibiotic agar__
    * __'plain' E.coli__ go on __'plain' agar__

## Day 2
If agar cultures are OK, then continue...
* Subculture __with-plasmid__ cells in __antibiotic__ broth
  * incubate in shaker incubator (broth is shaking)

## Day 3
* perform plasmid extraction on 'with-plasmid' cell broth
  * label plasmid extract and place on ice
  * make agarose gel in microwave, pulsing 10 seconds at a time
  * prepare the gel tray by taping the open ends with masking tape
  * place gel comb in the tray at the side notches
  * cast the agarose into the gel tray
  * once cool, remove the masking tape and comb
  * place into the gel box
  * prepare gel electrophoresis buffer solution
  * pour buffer over the top of the gel, covering it by at least 5 millimeters
  * into a new tube, mix 2 μL loading dye per 10 μL of DNA sample.
  * Load 12 μL prepared ladder 
    * Typically load ladder in left-most lane and sometimes right-most lane as well depending on whether you have the space.
  * Load 2 samples left to right. 
    * Load 12 μL into each well
  * connect the gel box to the electrphoresis power supply
    * run at ~85 volts for 1 hr 20 mins
      * or 95 Volts for less than an hour
  * remove gel from gel box
  * stain gel with post-stain (GelGreen or GelRed equivalent) 
  * visualize with gel imager

__If plasmid-prep OK, then continue...__
* Subculture __'plain'__ cells in __'plain'__ broth
  * incubate in shaker incubator (broth is shaking)

## Day 3.5
* Concentrate the cells, chill, add DNA
* electroporate
* incubate during recovery
* plate recovered transformants on petri dishes __with antibiotic__ (use cell-spreader)
  * use 3 petri dishes, with 50 μL of cell suspension each
* plate recovered transformants on petri dish with __plain__ agar
  * this will be used to calculate transformation efficiency

## Day 4
* Check the petri dishes for colonies
* count the number of colonies on each of the (3) antibiotic plates, and the (1) 'plain' control plate
* the number of antibiotic cells divided by the number of plain-agar cells will tell us, of the cells which survived the shocking experience, what proportion took up the plasmid (possesing the antiobiotic resistance gene for selection)

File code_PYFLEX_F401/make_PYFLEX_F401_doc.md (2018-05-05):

# Flashing MicroPython
## PYFLEX_F401
* `git clone https://github.com/micropython/micropython.git`
* ``export UPYTHON_HOME=`realpath micropython` ``
* `export BOARD=PYFLEX_F401`
* `cd $UPYTHON_HOME`
* `git checkout 68f4cba3d2aa056f305a20c9e394d4ebf81869ce`
* __patch with ADC DMA sampling changes__
  * `patch -p1 ./ports/stm32/adc.c < ../culture_shock/FOR_ADC_DMA__adc.c.patch`
    * assumes culture_shock and micropython repos are in the same directory
    * hacks the __read_timed__ method, and adds a new method __read_timed_stop__
* `cd ports/stm32/boards/`
* `git clone https://github.com/jgriessen/PYFLEX_F401.git`
  * if you don't already have it
* `cd ..`
* on PYFLEX board
  * press & hold    __SW23__ (boot0 switch)
  * press & release __SW22__ (reset switch)
* `make BOARD=PYFLEX_F401`
  * make refers to micropython/ports/stm32/Makefile.
* __if you need to erase the program area, i.e. if you wrote bad MicroPython code that "bricked" the MCU__
  * (Starting from the same directory as above -- micropython/ports/stm32)
  * `dfu-util -v -s :mass-erase:force -a 0 -d 0483:df11 -D build-G30TH/firmware.dfu`
* `make BOARD=PYFLEX_F401 deploy`

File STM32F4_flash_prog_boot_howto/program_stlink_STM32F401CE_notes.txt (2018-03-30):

john@ecolab3 [STM32F4_micropython_openocd]cat program_stlink_STM32F401CE.sh 
#!/bin/bash
# program_stlink_STM32F401CE.sh

openocd   -f interface/stlink.cfg -f target/stm32f4x.cfg -c "program ./g30th_firmware0.bin 0x08000000 verify; program ./g30th_firmware1.bin 0x08020000 verify reset exit"
john@ecolab3 [STM32F4_micropython_openocd]./program_stlink_STM32F401CE.sh 
Open On-Chip Debugger 0.10.0+dev-00364-g1756f393 (2018-03-27-21:22)
Licensed under GNU GPL v2
For bug reports, read
	http://openocd.org/doc/doxygen/bugs.html
Info : auto-selecting first available session transport "hla_swd". To override use 'transport select <transport>'.
Info : The selected transport took over low-level target control. The results might differ compared to plain JTAG/SWD
adapter speed: 2000 kHz
adapter_nsrst_delay: 100
none separate
Info : Unable to match requested speed 2000 kHz, using 1800 kHz
Info : Unable to match requested speed 2000 kHz, using 1800 kHz
Info : clock speed 1800 kHz
Info : STLINK v2 JTAG v30 API v2 SWIM v19 VID 0x0483 PID 0x374B
Info : using stlink api v2
Info : Target voltage: 3.261660
Info : stm32f4x.cpu: hardware has 6 breakpoints, 4 watchpoints
Info : Listening on port 3333 for gdb connections
Info : Unable to match requested speed 2000 kHz, using 1800 kHz
Info : Unable to match requested speed 2000 kHz, using 1800 kHz
adapter speed: 1800 kHz
target halted due to debug-request, current mode: Thread 
xPSR: 0x01000000 pc: 0xfffffffe msp: 0xfffffffc
Info : Unable to match requested speed 8000 kHz, using 4000 kHz
Info : Unable to match requested speed 8000 kHz, using 4000 kHz
adapter speed: 4000 kHz
** Programming Started **
auto erase enabled
Info : device id = 0x10006433
Info : flash size = 512kbytes
target halted due to breakpoint, current mode: Thread 
xPSR: 0x61000000 pc: 0x20000046 msp: 0xfffffffc
wrote 16384 bytes from file ./g30th_firmware0.bin in 1.013997s (15.779 KiB/s)
** Programming Finished **
** Verify Started **
target halted due to breakpoint, current mode: Thread 
xPSR: 0x61000000 pc: 0x2000002e msp: 0xfffffffc
verified 14932 bytes in 0.374018s (38.988 KiB/s)
** Verified OK **
Info : Unable to match requested speed 2000 kHz, using 1800 kHz
Info : Unable to match requested speed 2000 kHz, using 1800 kHz
adapter speed: 1800 kHz
target halted due to debug-request, current mode: Thread 
xPSR: 0x01000000 pc: 0x0804952c msp: 0x20018000
Info : Unable to match requested speed 8000 kHz, using 4000 kHz
Info : Unable to match requested speed 8000 kHz, using 4000 kHz
adapter speed: 4000 kHz
** Programming Started **
auto erase enabled
wrote 393216 bytes from file ./g30th_firmware1.bin in 9.684025s (39.653 KiB/s)
** Programming Finished **
** Verify Started **
target halted due to breakpoint, current mode: Thread 
xPSR: 0x61000000 pc: 0x2000002e msp: 0x20018000
verified 284016 bytes in 0.862018s (321.756 KiB/s)
** Verified OK **
** Resetting Target **
Info : Unable to match requested speed 2000 kHz, using 1800 kHz
Info : Unable to match requested speed 2000 kHz, using 1800 kHz
adapter speed: 1800 kHz
shutdown command invoked

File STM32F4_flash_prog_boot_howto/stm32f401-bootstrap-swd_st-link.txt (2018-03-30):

1	Leave both boot jumpers to "0".
2 	Have OpenOCD installed,
	git clone https://git.code.sf.net/p/openocd/code openocd-code
	
3	a file in /etc/udev/rules.d
4	Assuming a Linux host and system-wide default OpenOCD installation, check if connectivity is okay, the MCU is alive, and OpenOCD can talk to it:

     openocd -f interface/stlink-v2.cfg -f target/stm32f1x_stlink.cfg

Depending on the OpenOCD version, the following may also work:

     openocd -f interface/stlink-v2.cfg -f target/stm32f1x.cfg

If things are good, OpenOCD will print some information about the MCU (voltage, number of HW breakpoints, etc) and keep running.

5	

5    	It may be possible to run OpenOCD as a daemon and use telnet to use it, but I think it is more convenient to start it every
	time. Assuming you have a properlycompiled binary, let's say, blinky.bin, you can program it into the MCU with the following script:
	
	OPENOCD="openocd -f interface/stlink-v2.cfg -f target/stm32f1x_stlink.cfg"
    	$OPENOCD -c "init" -c "reset halt" -c "stm32f1x mass_erase 0" -c "flash write_bank 0 blinky.bin 0" -c "reset run" -c "shutdown"

	Note that there is the file name inside this script that you will need to adjust. 
	It is probably a good idea to start with something really simple.

========================use the "program" helper of openocd to laod code===================
configure OpenOCD and start it up.

A simple way to organize them all involves keeping a single directory for your work with a given board. When you start OpenOCD from that directory, it searches there first for configuration files, scripts, and for code you upload to the target board.  It is also the natural place to write files, such as log files and data you download from the board. 

how you start the server:

    Many -f file or -c command options on the command line
    No options, but a user config file in the current directory named openocd.cfg 

Config files:
======================
Three main types of non-user configuration file each have their own subdirectory in the scripts directory:

    interface – one for each different debug adapter;
    board – one for each different board
    target – the chips which integrate CPUs and other JTAG TAPs 

Best case: include just two files, and they handle everything else. The first is an interface config file. The second is board-specific, and it sets up the JTAG TAPs and their GDB targets (by deferring to some target.cfg file), declares all flash memory, and leaves you nothing to do except meet your deadline:

source [find interface/olimex-jtag-tiny.cfg]
source [find board/csb337.cfg]

Boards with a single microcontroller often won’t need more than the target config file, as in the AT91SAM7X256 example. That’s because there is no external memory (flash, DDR RAM), and the board differences are encapsulated by application code.
Maybe you don’t know yet what your board looks like to JTAG. Once you know the interface.cfg file to use, you may need help from OpenOCD to discover what’s on the board. Once you find the JTAG TAPs, you can just search for appropriate target and board configuration files ... or write your own, from the bottom up. See Autoprobing.
You can often reuse some standard config files but need to write a few new ones, probably a board.cfg file. You will be using commands described later in this User’s Guide, and working with the guidelines in the next chapter. 

========================use the "program" helper of openocd to laod code===================

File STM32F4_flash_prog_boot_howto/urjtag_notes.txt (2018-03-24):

TRST-: Resets the JTAG TAP controller and the CPU internal debug logic.
SRST-: Resets the CPU core and peripherals

 "SVF should be generated with only one device in the chain". It doesn't mean that you're restricted with it to chains with only a single device in them. It just means that SVF player can operate only on a single device at once, but you can select this single device in a chain of multiple devices beforehand. The documentation about svf describes in detail how to select the target:

http://urjtag.org/book/_jtag_commands.html#_svf

Kolja

The Standard Test And Programming Language (STAPL) format serves for
describing actions over JTAG interfaces. The STAPL is standardized in
JEDEC "JESD-71" (http://www.jtagtest.com/pdf/jesd71_stapl.pdf). This
version of the standard was developed by Altera and released to public
(read Altera license in enclosed COPYING file). However, it does not
cover the whole standard. Afterwards, Actel extended the code about
EXPORT command to be compatible with STAPL files generated by Actel
Libero IDE Suite. Now, the development is running separately. The idea
is to incorporate STAPL player into UrJTAG; thus, unite the
development and contribute from the support of vast number of JTAG
devices. Then, UrJTAG will become even more versatile software
package.

Compiled with latest STAPL feature 

cd urjtag/urjtag
./autogen.sh
./configure --enable-stapl
make

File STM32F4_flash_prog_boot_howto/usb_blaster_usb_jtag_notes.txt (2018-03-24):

USB BLASTER cheap Rev.c clone. The original uses FTDI FT245 and MAX CPLD chips. This one uses a Silicon Labs C8051F321 micro-controller and a 74LVC125 quad buffer, but there are many other clone variants.

COMMON ISSUES: I received a number of mails from others who used my logic with
varying success. Following are some general tips.

If it works "partially" for you, "sometimes" or "it programs the device, but
the device doesn't work afterwards", your setup maybe isn't suitable for clear
transmission of signals at several MHz. It may still be a critical timing in
the logic, but I'm using it even slightly "overclocked" at 25 MHz and haven't
had any errors since months. So I doubt it's the logic. Try reducing the clock
to the CPLD from 24 MHz to, say, 6 MHz.

=============================

:!: be aware that here the VCC{TARGET} pin has to be connected to a reference voltage used for the JTAG communication, generally provided by the target device on the board (often 3.3V or 1.8V). Else the signals can not be detected by the JTAG adapter. 

add the rules for normal users to be able to access the device (udev rule based on the VID and PID shown by lsusb). This has only to be done once, before the device is plugged in to be used:

echo -n 'Altera USB-Blaster JTAG adatper' | sudo tee -a /etc/udev/rules.d/60-altera-usb-blaster.rules
echo -n 'ATTR{idVendor}=="09fb", ATTR{idProduct}=="6001", MODE="666"' | sudo tee -a /etc/udev/rules.d/60-altera-usb-blaster.rules
sudo udevadm control --reload-rules

 use the USB-Blaster emulation firmware from http://www.ixo.de/info/usb_jtag/ with the usbblaster cable driver. 

 Kolja Waschk <kawk@ix...   2017-03-01 15:22:18

> How about a new release after 8 years? =)

Hi,

I started to sort some of the existing issues so that resolved ones 
since 0.10 now have a new tag '0.17', preparing a release with proper 
NEWS info. But then somehow stopped activity, waiting for further info 
from Mike about his plans (he created the UrJTAG org at github..?

Kolja Waschk, January 2007

 January 2007, 12:23 In principle, you could re-program an USB Blaster CPLD with my VHDL code (after you defined the correct IO pin assignments) and the device would still appear to be an USB Blaster and could be used as before with Quartus etc.
But it's not exactly the same. I don't know the exact contents of the CPLD in the Blaster. Probably some situations exist in which the Altera device performs better than mine.

I don't have detailed schematics. For my tests I just wired a FTDI module with FT245RL directly to an EPM7064 with a few external resistors and pinheader for the JTAG connection, exactly as documented in their respective datasheets.

Kolja 

https://www.eevblog.com/forum/microcontrollers/altera-usb-programmer/ Re: Altera USB Programmer « Reply #21 on: November 16, 2013, 02:55:24 PM 
»[ had a look at the VHDL code, the CPLD handles all the control of the JTAG state machine, leaving the MCU to simply stream the data in and out.]

but, does it work with F401 errata whee hardware flow control is broken?

============================================
5th July 2008, 12:11
Original USB Blaster can be expected to stream bulk data with nearly full rate of 6 MBit/s. Most @ltera FPGA would support higher JTAG speed. About the FX2 solution?
The maximum bit rate is 3 MHz with the FX2, but because it also has to handle the USB protocol in software, the maximum througput is probably less. In daily work it appears to be "a little slower" than an USB-Blaster.

Kolja 

==============
James B   https://alteraforum.com/forum/archive/index.php/t-39001.html
January 9th, 2013, 10:16 AM
3) Hypothesizing that the Altera Programmer does not enable flow-control in the FTDI drivers that are used for the USB-Blaster interface, I relaxed the timing in my UM232H controller interface to slow down the interface. After few iterations, the USB-Blaster clone started working.

=====================================

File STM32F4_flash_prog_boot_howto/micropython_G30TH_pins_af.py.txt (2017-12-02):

The Pin and PinAF data structures are currently all generated programmatically. 
You can look at the underlying data by looking at the pins_BOARDNAME.c in the build-BOARDNAME directory.
 A snippet looks like this:
const pin_af_obj_t pin_A0_af[] = {
  AF( 1, TIM     ,  2, CH1       , TIM2    ), // TIM2_CH1
  AF( 1, TIM     ,  2, ETR       , TIM2    ), // TIM2_ETR
  AF( 2, TIM     ,  5, CH1       , TIM5    ), // TIM5_CH1
#if defined(MICROPY_HW_UART2_PORT)
  AF( 7, USART   ,  2, CTS       , USART2  ), // USART2_CTS
#endif
  //(15, EVENTOUT,  0,           , EVENTOUT), // EVENTOUT
};

const pin_obj_t pin_A0 = PIN(A, 0, pin_A0_af, PIN_ADC1, 0);

const pin_af_obj_t pin_A1_af[] = {
  AF( 1, TIM     ,  2, CH2       , TIM2    ), // TIM2_CH2
  AF( 2, TIM     ,  5, CH2       , TIM5    ), // TIM5_CH2
#if defined(MICROPY_HW_UART2_PORT)
  AF( 7, USART   ,  2, RTS       , USART2  ), // USART2_RTS
#endif
  //(15, EVENTOUT,  0,           , EVENTOUT), // EVENTOUT
};

const pin_obj_t pin_A1 = PIN(A, 1, pin_A1_af, PIN_ADC1, 1);
---------------------------------------------------------------
, 1);  is for PA1 AF01

======================================
Looking at the datasheet, CAN2_TX is alternate function 9 on pin B13. So even though we didn't create a constant for it, you can do this:

Code: Select all

can_tx = pyb.Pin(pyb.Pin.cpu.B13, pyb.Pin.AF_PP, pyb.Pin.PULL_NONE, 9)
=============================================================================
To configure X3 to expose TIM2_CH3, you could use:

pin = pyb.Pin(pyb.Pin.board.X3, mode=pyb.Pin.AF_PP, af=pyb.Pin.AF1_TIM2)

or:

pin = pyb.Pin(pyb.Pin.board.X3, mode=pyb.Pin.AF_PP, af=1)

=====================USB VBUS======================================
The 500 mA is a requirement for USB HOST. This supply number is frequently confused with a requirement for a USB DEVICE as consumer. A USB device SHOULD NOT draw more than 100 mA upon initial connect stage, and can draw full power only when it gets enumerated and receives "set_configuration ()" command. 

    NOTE1: VBUS must be supplied by host even in "sleep" (suspend state) mode.

--

    NOTE2: if a host doesn't drive VBUS high, no attachment would/should occur, even if the device has own power. Connect requests (D+ or D- pull-ups) must occur only if VBUS is present, by USB 2.0 specifications Sec.7.2.1. So it is a spec violation just to "have" the pull-ups, the pull-up must be conditional with VBUS.

things are a bit different with introduction of Type-C connector. Type-C devices (both hosts and peripherals) are prohibited to output VBUS, initially. So, instead of boldly having VBUS power on a Type-C port, the host must turn on VBUS source only if the port logic detects the presence of cable/device. It does this by sensing voltage level on "CC" (Communication Channel) pin. A Type-C host has a pull-up on both CC pins. A device (or legacy cable assembly) must have 5.1k pull-down. When device/cable is plugged in, the host detects that 5.k drags its pull-up down, and at this point the host has rights to engage VBUS power, and USB communication begins.

pyflex_f401 is a USB device not a host, so VBUS is just for use in handshaking with hosts, not suppoying power to other USB devices.  The software overhead is huge for that.
====================================================

Pin.init(mode, pull=Pin.PULL_NONE, af=-1)

    Initialise the pin:

            mode can be one of:

                    Pin.IN - configure the pin for input;
                    Pin.OUT_PP - configure the pin for output, with push-pull control;
                    Pin.OUT_OD - configure the pin for output, with open-drain control;
                    Pin.AF_PP - configure the pin for alternate function, pull-pull;
                    Pin.AF_OD - configure the pin for alternate function, open-drain;
                    Pin.ANALOG - configure the pin for analog.

            pull can be one of:

                    Pin.PULL_NONE - no pull up or down resistors;
                    Pin.PULL_UP - enable the pull-up resistor;
                    Pin.PULL_DOWN - enable the pull-down resistor.

            when mode is Pin.AF_PP or Pin.AF_OD, then af can be the index or name of one of the alternate functions associated with a pin.

    Returns: None.
======================================================================================
you'll see that each AF is really just the number that corresponds to the digit after the AF. So each of these is the same:

Code: Select all

>>> p = pyb.Pin('A0', mode=pyb.Pin.AF_PP, af=pyb.Pin.AF3_TIM8)
>>> p
Pin(Pin.cpu.A0, mode=Pin.ALT, af=Pin.AF3_TIM8)
>>> p = pyb.Pin('A0', mode=pyb.Pin.AF_PP, af=3)
>>> p
Pin(Pin.cpu.A0, mode=Pin.ALT, af=Pin.AF3_TIM8)
==========================================================

PINS_AF = (
  ('JP3', (1, 'TIM1_CH2'), (7, 'USART1_TX'), ),
  ('JP4', (1, 'TIM1_CH3'), (7, 'USART1_RX'), ),
  ('JP5', (1, 'TIM1_CH1'), (4, 'I2C3_SCL'), (7, 'USART1_CK'), ),
  ('JP6', (2, 'TIM3_CH4'), (4, 'I2C3_SDA'), ),
  ('JP7', (2, 'TIM3_CH3'), (8, 'USART6_CK'), ),
  ('JP8', (6, 'SPI3_SCK'), (6, 'I2S3_CK'), ),
  ('JP9', (5, 'I2S3_EXTSD'), (6, 'SPI3_MISO'), ),
  ('JP10', (6, 'SPI3_MOSI'), (6, 'I2S3_SD'), ),
  ('JP11', (2, 'TIM3_ETR'), ),
  ('JP12', (1, 'TIM2_CH2'), (5, 'SPI1_SCK'), (6, 'SPI3_SCK'), (6, 'I2S3_CK'), (9, 'I2C2_SDA'), ),
  ('JP13', (2, 'TIM3_CH1'), (5, 'SPI1_MISO'), (6, 'SPI3_MISO'), (7, 'I2S3_EXTSD'), (9, 'I2C3_SDA'), ),
  ('JP14', (2, 'TIM3_CH2'), (5, 'SPI1_MOSI'), (6, 'SPI3_MOSI'), (6, 'I2S3_SD'), ),
  ('JP15', (2, 'TIM4_CH1'), (4, 'I2C1_SCL'), (7, 'USART1_TX'), ),
  ('JP16', (2, 'TIM4_CH2'), (4, 'I2C1_SDA'), (7, 'USART1_RX'), ),
  ('JP17', (1, 'TIM1_CH1N'), (5, 'SPI2_SCK'), (5, 'I2S2_CK'), ),
  ('JP18', (1, 'TIM1_CH2N'), (5, 'SPI2_MISO'), (6, 'I2S2_EXTSD'), ),
  ('JP19', (1, 'TIM1_CH3N'), (5, 'SPI2_MOSI'), (5, 'I2S2_SD'), ),
  ('JP21', ),
  ('JP22', ),
  ('JP23', (5, 'SPI2_MISO'), (6, 'I2S2_EXTSD'), ),
  ('JP24', (5, 'SPI2_MOSI'), (5, 'I2S2_SD'), ),
  ('JP25', (1, 'TIM2_CH1'), (1, 'TIM2_ETR'), (2, 'TIM5_CH1'), (7, 'USART2_CTS'), ),
  ('JP26', (1, 'TIM2_CH2'), (2, 'TIM5_CH2'), (7, 'USART2_RTS'), ),
  ('JP27', (1, 'TIM2_CH3'), (2, 'TIM5_CH3'), (3, 'TIM9_CH1'), (7, 'USART2_TX'), ),
  ('JP28', (1, 'TIM2_CH4'), (2, 'TIM5_CH4'), (3, 'TIM9_CH2'), (7, 'USART2_RX'), ),
  ('JP29', (5, 'SPI1_NSS'), (6, 'SPI3_NSS'), (6, 'I2S3_WS'), (7, 'USART2_CK'), ),
  ('JP30', (1, 'TIM2_CH1'), (1, 'TIM2_ETR'), (5, 'SPI1_SCK'), ),
  ('JP31', (2, 'TIM4_CH4'), (3, 'TIM11_CH1'), (4, 'I2C1_SDA'), (5, 'SPI2_NSS'), (5, 'I2S2_WS'), ),
  ('JP32', (2, 'TIM4_CH3'), (3, 'TIM10_CH1'), (4, 'I2C1_SCL'), ),
  ('JP33', ),
  ('JP34', (1, 'TIM2_CH1'), (1, 'TIM2_ETR'), (5, 'SPI1_NSS'), (6, 'SPI3_NSS'), (6, 'I2S3_WS'), ),
  ('JP35', (1, 'TIM2_CH3'), (4, 'I2C2_SCL'), (5, 'SPI2_SCK'), (5, 'I2S2_CK'), ),
  ('SD', ),
  ('SC', ),
  ('B1', ),
)

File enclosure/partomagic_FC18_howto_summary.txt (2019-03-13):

Part-o-Magic has a few limitations:
Avoid PartDesign datum lines.

-----------------Part-o-Magic allows containers of containers------------------

to have "Part002" inside "Part", activate "Part" before creating "Part002"   (leave and enter buttons)

PoM always adds whatever is created to active container.

To add another Part to the root of document, deactivate whatever is active, activate root, add another Part.

-----------------Part-o-Magic allows containers of containers------------------

start from sketcher workbench to make a part-o-magic extrusion, ( do not use PartDesign workbench)

What I see in your project looks like you want to subtract sweep from cone. If so:
1. enter SubtractiveShape
-> nothing is visible, but it should be. I don't know what's going on, but let's ignore it for a moment.
2. select cs-enc-bosses-subtract and invoke "Set Tip" command from part-o-magic
3. leave SubtractiveShape, and make the last feature of cs-enc-back-floor-n-bosses visible. You should see your cone got cut by the sweep.

==============================PartDesign Body=====================
Base Feature

The base feature is by definition the first PartDesign feature created in the Body. But it is possible to use a solid shape, either imported or modelled in other workbenches, as a base feature to which sketches and other features can be added.
PartDesign Body tree-03.png
Tip

The tip is the feature that is exposed outside the Body. It is automatically set to the last feature at the bottom of the tree. But sometimes it can be useful to change it to an earlier feature in the Body tree, which in effect rolls back its history; then it is possible to add features that should have been added earlier. In the Body tree, the feature set to tip displays a green dot with a white down arrow in it.
PartDesign Body tree-04.png

For more details, see the PartDesign MoveTip.png Move Tip page.
Visibility Management

The Body's visibility supersedes the visibility of any object it contains. If the Body is hidden, the objects it contains will be hidden as well, even if their visibility is set to true. Only one feature can be visible at a time. Selecting a hidden feature and pressing the space bar will make it visible, and automatically hide the previously visible feature.
Interaction with other workbenches

By default, objects underneath a Body are selectable, and this is of course required to edit and add features in PartDesign. But selecting a Body's features to create operations from other workbenches (like Part or Draft) is not advised, as the results may be unexpected; in all cases, an error labelled Links go out of the allowed scope will appear in the Report view.

Therefore, for interactions with other workbenches, only the Body itself should be selected from the Model tree. In cases where it is necessary to select specific topology on the Body (vertex, edge, face), then the Body's Display Mode Body view property can be switched from Through (default) to Tip. This property is accessible from the View panel. In Tip mode, access to the objects under the Body (features, datums, sketches) is disabled; everything but the tip feature will be hidden in the 3D view, no matter which object is set as visible.

Once operations in other workbenches are completed, do not forget to reset the Display Mode Body property to Through to be able to edit the Body.
How to use

    Press the PartDesign Body.png Create body button. The new body automatically becomes active.
    Double-click the Body in the Model tree or right-click and select Toggle active body to activate or deactivate a body. If another body is already active, it will be automatically deactivated.
    If a solid shape is selected first, a BaseFeature solid object is added to the Body; the BaseFeature is linked to the original solid shape. Accepted shapes can be an imported solid, or a solid made in any other FreeCAD workbench.
    In a new document, if a sketch is created from the PartDesign workbench toolbar, a new Body will be automatically created.

Properties

    VIEWDisplay Mode Body: sets the display between two modes:
        Through (default) exposes everything inside the body (features, datums, sketches, etc.). It is the mode used in adding and editing features inside the body.
        Tip exposes only the shape of the Body itself according to the set tip; everything else including sketches is hidden from view and cannot be displayed. Practical use: "Tip" allows selection of edges and faces of the Body to create operations from other workbenches.
    DATATip: displays/sets the feature defined as tip.
    DATABase Feature: displays/sets the external shape used as base feature. Does not apply if a PartDesign feature is the base feature.
    DATAPlacement: specifies the orientation and position of the Body in the 3D space. See Placement.
    DATALabel: the Label is the name given to the operation. This name can be changed at your convenience.
    DATAGroup: lists the referenced objects inside the Body.

==============================PartDesign Body=====================

-----------------------------------sweeps--------------------------------

PartDesign additive pipe can be pressed after selecting a profile sketch.  The profile must already be oriented perpendicular to the starting point of a section of the sweep outline,
and offset so it is at the starting point also.  Next choose [add edge] button and select the segment to start the sweep with.  
Display updates rendering a translucent version of the sweep up to that section end point.  Repeat adding edges one at a time until all there.  Click OK.

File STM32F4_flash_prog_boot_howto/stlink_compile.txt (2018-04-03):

========compiling stlink================
rshell needs the open source stlink setup to use nucleo boards...
https://github.com/texane/stlink

clone the source to either your user home dir, or /usr/local/src
get dependencies installed on your system:

sudo apt-get install cmake
sudo apt-get install libusb-1.0-0-dev
sudo apt-get install libgtk-3-dev

cd stlink
sudo mkdir build 
cd build
sudo cmake -DCMAKE_BUILD_TYPE=Debug ..
sudo make
# Setup udev to create USB ports.  Since we are using a nucleo board with ST-Link version 2-1,
# choose from /usr/local/src/stlink/etc/udev/rules.d
# the file 49-stlinkv2-1.rules
sudo cp 49-stlinkv2-1.rules /etc/udev/rules.d
# restart udev so the USB device will pop on and off as it is plugged in
sudo udevadm control --reload-rules
sudo udevadm trigger

# Now copy the built executables to a reasonable place such as ~/bin
# or /usr/local/bin

sudo cp st-flash st-info stlink-gui stlink-gui-local st-term st-util /usr/local/bin

# Now try plugging the nucleo-F401RE into a USB port of the devel machine, then if you get results
# like below, your tools for flashing micropython are ready:
john@ecolab3 [~]ll /dev/stl*
lrwxrwxrwx 1 root root  3 Jun 29 09:38 /dev/stlinkv2-1_ -> sdb
lrwxrwxrwx 1 root root 11 Jun 29 09:38 /dev/stlinkv2-1_0 -> bsg/5:0:0:0
lrwxrwxrwx 1 root root  3 Jun 29 09:38 /dev/stlinkv2-1_2 -> sg2
john@ecolab3 [~]which st-flash
/usr/local/bin/st-flash

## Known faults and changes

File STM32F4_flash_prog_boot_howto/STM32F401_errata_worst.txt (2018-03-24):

select the JTAG-DP or the SW-DP
asynchronous trace can only be used with SW-DP, not JTAG-DP, since
they share a pin.

SDW-->trace
 JTAG-DP-->scan boundary chains

SD card:
SDIO HW flow control
Description
When enabling the HW flow control by setting 
bit 14 of the SDIO_CLKCR register to ‘1’, 
glitches can occur on the SDIOCLK output clo
ck resulting in wrong data to be written into 
the SD/MMC card or into the SDIO device. 
As a consequence, a CRC error will be reported 
to the SD/SDIO MMC host interface (DCRCFAIL 
bit set to ‘1’ in SDIO_STA register). 
Workaround
None. 
Note:
Do not use the HW flow control. Overrun errors (Rx mode) and FIFO underrun (Tx mode) 
should be managed by the application software.

I think this might be workable by setting the clock speed of the jtag_usb usb_blaster to a chunk less than the MCU clock for serial data...

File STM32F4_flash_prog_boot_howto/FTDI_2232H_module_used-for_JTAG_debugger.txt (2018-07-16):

See culture_shock/JTAG_debugger symlink for notes on using the FT2232H.
This symlinked directory is in .gitignore and is not part of this repo.

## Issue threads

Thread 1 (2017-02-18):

### ISSUE TITLE
If gEDA supports multiple net-names for a net (aliases?), could we get some more verbose net-names?

### ISSUE THREAD

**Issue by nmz787** [kanzure/culture_shock#1]
For example, PA4 appears to be coming off a voltage divider and heading to the STM32's ADC1 input (which is muxed on PA4, according to the controller's datasheet). If gEDA can support multiple net-names on a net, then it would be nice to add another name to the PA4 net... HV_SENSE or something.

**Comment by jgriessen** [comment]
Sure thing Nathan.  I'll make them like PA4_HV_SENSE.  HV_SENSE is just right as a name for this.  Thanks for reviewing.

**Comment by nmz787** [comment]
Issue was solved [in this commit](https://github.com/kanzure/culture_shock/blob/04f44e49732baf2d4784e47160a141f80ddaa6bb/kvboard.sch)
and schematic PNG updated [in this commit](https://github.com/kanzure/culture_shock/commit/39a35a4c5a8d66eba69640c86b20827881aa05fd)

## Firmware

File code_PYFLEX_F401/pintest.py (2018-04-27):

import machine
import pyb
# Define pins so they can be set with a pin reference like:  pin10.value(1) on the fly.
pinA1 = machine.Pin(machine.Pin.cpu.A1, machine.Pin.OUT_PP, machine.Pin.PULL_NONE)
pinA2 = machine.Pin(machine.Pin.cpu.A2, machine.Pin.OUT_PP, machine.Pin.PULL_NONE)
pinA3 = machine.Pin(machine.Pin.cpu.A3, machine.Pin.OUT_PP, machine.Pin.PULL_NONE)
pinA4 = machine.Pin(machine.Pin.cpu.A4, machine.Pin.OUT_PP, machine.Pin.PULL_NONE)
pinA5 = machine.Pin(machine.Pin.cpu.A5, machine.Pin.OUT_PP, machine.Pin.PULL_NONE)
pinA6 = machine.Pin(machine.Pin.cpu.A6, machine.Pin.OUT_PP, machine.Pin.PULL_NONE)
pinA7 = machine.Pin(machine.Pin.cpu.A7, machine.Pin.OUT_PP, machine.Pin.PULL_NONE)
pinA8 = machine.Pin(machine.Pin.cpu.A8, machine.Pin.OUT_PP, machine.Pin.PULL_NONE)
pinA9 = machine.Pin(machine.Pin.cpu.A9, machine.Pin.OUT_PP, machine.Pin.PULL_NONE)
pinA10 = machine.Pin(machine.Pin.cpu.A10, machine.Pin.OUT_PP, machine.Pin.PULL_NONE)
pinA11 = machine.Pin(machine.Pin.cpu.A11, machine.Pin.OUT_PP, machine.Pin.PULL_NONE)
pinA12 = machine.Pin(machine.Pin.cpu.A12, machine.Pin.OUT_PP, machine.Pin.PULL_NONE)
pinA13 = machine.Pin(machine.Pin.cpu.A13, machine.Pin.OUT_PP, machine.Pin.PULL_NONE)
pinA14 = machine.Pin(machine.Pin.cpu.A14, machine.Pin.OUT_PP, machine.Pin.PULL_NONE)
pinA15 = machine.Pin(machine.Pin.cpu.A15, machine.Pin.OUT_PP, machine.Pin.PULL_NONE)

pinB3 = machine.Pin(machine.Pin.cpu.B3, machine.Pin.OUT_PP, machine.Pin.PULL_NONE)
pinB4 = machine.Pin(machine.Pin.cpu.B4, machine.Pin.OUT_PP, machine.Pin.PULL_NONE)
pinB5 = machine.Pin(machine.Pin.cpu.B5, machine.Pin.OUT_PP, machine.Pin.PULL_NONE)
pinB6 = machine.Pin(machine.Pin.cpu.B6, machine.Pin.OUT_PP, machine.Pin.PULL_NONE)
pinB7 = machine.Pin(machine.Pin.cpu.B7, machine.Pin.OUT_PP, machine.Pin.PULL_NONE)
pinB8 = machine.Pin(machine.Pin.cpu.B8, machine.Pin.OUT_PP, machine.Pin.PULL_NONE)
pinB9 = machine.Pin(machine.Pin.cpu.B9, machine.Pin.OUT_PP, machine.Pin.PULL_NONE)
pinB10 = machine.Pin(machine.Pin.cpu.B10, machine.Pin.OUT_PP, machine.Pin.PULL_NONE)
pinB13 = machine.Pin(machine.Pin.cpu.B13, machine.Pin.OUT_PP, machine.Pin.PULL_NONE)
pinB14 = machine.Pin(machine.Pin.cpu.B14, machine.Pin.OUT_PP, machine.Pin.PULL_NONE)
pinB15 = machine.Pin(machine.Pin.cpu.B15, machine.Pin.OUT_PP, machine.Pin.PULL_NONE)

count = 0
while ( count < 40):
    pinA12.value(0)
#    pinB5.value(0)
#    pinB3.value(0)
#    pinB4.value(0)
    pinB8.value(0)
    pinB9.value(0)
    pyb.delay(60)
    pinA12.value(1)
#    pinB5.value(1)
#    pinB3.value(1)
#    pinB4.value(1)
    pinB8.value(1)
    pinB9.value(1)
    pyb.delay(60)
    count = count + 1

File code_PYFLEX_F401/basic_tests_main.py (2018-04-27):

# main.py -- Define pins so they can be set with a pin reference like:  pin10.value(1) on the fly.
import machine
import pyb
uart = pyb.UART(2, 4800)
pyb.repl_uart(uart)
pinB8 = machine.Pin(machine.Pin.cpu.B8, machine.Pin.OUT_PP, machine.Pin.PULL_NONE)
pinB9 = machine.Pin(machine.Pin.cpu.B9, machine.Pin.OUT_PP, machine.Pin.PULL_NONE)
pinA8 = machine.Pin(machine.Pin.cpu.A8, machine.Pin.OUT_PP, machine.Pin.PULL_NONE)
pinA5 = machine.Pin(machine.Pin.cpu.A5, machine.Pin.OUT_PP, machine.Pin.PULL_NONE)
pinA4 = machine.Pin(machine.Pin.cpu.A4, machine.Pin.OUT_PP, machine.Pin.PULL_NONE)
pinB8.value(0)
pinB9.value(1)
pinA8.value(0)
pinA5.value(1)
pinA4.value(1)
pyb.delay(200)
pinB8.value(1)
pinB9.value(0)
pinA8.value(1)
pinA5.value(0)
pinA4.value(0)
pyb.delay(200)
pinB8.value(0)
pinB9.value(1)
pinA8.value(0)
pinA5.value(1)
pinA4.value(1)
pyb.delay(200)
pinB8.value(1)
pinB9.value(0)
pinA8.value(1)
pinA5.value(0)
pinA4.value(0)
pyb.delay(200)
pinB8.value(0)
pinB9.value(1)
pinA8.value(0)
pinA5.value(1)
pinA4.value(1)
pyb.delay(200)
pinB8.value(1)
pinB9.value(0)
pinA8.value(1)
pinA5.value(0)
pinA4.value(0)
pyb.delay(200)
pinB8.value(0)
pinB9.value(1)
pinA8.value(0)
pinA5.value(1)
pinA4.value(1)
pyb.delay(200)
pinB8.value(1)
pinB9.value(0)
pinA8.value(1)
pinA5.value(0)
pinA4.value(0)

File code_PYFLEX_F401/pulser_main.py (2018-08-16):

"""
Based on:
  example for:
  -- linked timers, slave in trigger mode, i.e. counter enabled from the master
  -- (slave) timer in one-pulse-mode with repetition
  https://community.st.com/thread/39151-one-pulse-with-repitition-counter

Definitions:

CEN -- The counter is clocked by the prescaler output CK_CNT, which is enabled only when the
      counter enable bit (CEN) in TIMx_CR1 register is set (refer also to the slave mode controller
      description to get more details on counter enabling).
      Note that the counter starts counting 1 clock cycle after setting the CEN bit in the TIMx_CR1
      register.

To get PA0 PA1 PA2 GPIOs to stay LO until wanted to go high, other setup is done after
      reset and soft reset:

      Setup is done right after imports with enable_gpio_and_timers(), then lots 
      of function defs and the "all good"  sequence of LED flashes and power supply turn on at the end.

      It is important to have the function timers_init() come before the power supply turn on.
"""


import micropython
micropython.alloc_emergency_exception_buf(100)
import stm
import pyb
import array
from math import ceil
from pyb import Timer
from machine import Pin
from machine import I2C
from stm_low_level import *
from nvic import *
try:
  import ssd1306
except:
  # OLED support won't be available
  pass


period = 265
width = 1
number_of_pulse_pairs = 5
common_prescaler = 11

enable_gpio_and_timers()
# PYFLEX_F401 pin LED_YELLOW,PB9  ==> pyflex_f401.sch LED_YELLOW,PB9
YEL_LED = Pin('LED_YELLOW', Pin.OUT) 
# EN_18V_ONBOARD is active HI, (drives base of Q32), U3_!SHDN is inverted EN_18V_ONBOARD.
EN_18V_ONBOARD = Pin('PB14', Pin.OUT) 
EN_18V_U4 = Pin('PB13', Pin.OUT) 


# Setup ADC Timer and a callback to try printing the value
#adc_vals = [-1 for i in range(number_of_pulse_pairs+1 if number_of_pulse_pairs+1 > 128 else 128)]
#t4 = pyb.Timer(4, prescaler=0, period=0)
#stm.mem16[stm.TIM4 + stm.TIM_CR1] &= (~1) & 0xFFFF# disable CEN
#adc_timer = t4.channel(4, pyb.Timer.PWM)#OC_TIMING, polarity=pyb.Timer.HIGH)
#stm.mem16[stm.TIM4 + stm.TIM_CR1] &= (~1) & 0xFFFF# disable CEN

# PYFLEX_F401 pin JA2 ==> pyflex_f401.sch JA2 ==> chip PA4
adc = pyb.ADC(pyb.Pin.board.JA2) 
adc_vals = array.array('H',[0 for i in range(2048)])
stm.mem32[stm.ADC1 + stm.ADC_CR2] |= 1   #enable ADC
adc.read_timed(adc_vals)
adc.read_timed_stop()


def reset_vals():
  global adc_vals
  for i in range(len(adc_vals)):
    adc_vals[i] = 0


### display
# create software mode (-1) I2C peripheral at frequency of 400kHz
# PYFLEX_F401 pin JB6,PB6 ==> pyflex_f401.sch JB6,PB6
# PYFLEX_F401 pin JB7,PB7 ==> pyflex_f401.sch JB7,PB7
i2c = I2C(-1, scl=pyb.Pin.board.JB6, sda=pyb.Pin.board.JB7, freq=40000) # was 400000
ssd = None

# scan for slaves, returning a list of 7-bit addresses
if i2c.scan():
  ssd = ssd1306.SSD1306_I2C(128, 64, i2c, addr=0x3c)

# just a fun test for displaying text
def banner():
  # text, x, y, color
  ssd.framebuf.text('Culture_Shock!',0,0, 0xffff)
  ssd.framebuf.text('by', 0, 18, 0xffff)
  ssd.framebuf.text('JohnG', 0, 27, 0xffff)
  ssd.framebuf.text('NMZ787', 0, 36, 0xffff)
  ssd.framebuf.text('and kanzure!', 0, 45, 0xffff)
  ssd.show()

if ssd:
  banner()

# some test content for the OLED graphing, should result in a triangle
def test_graph():
  global adc_vals
  f=0
  for i in range(len(adc_vals)):
    # increase the value until the half-way point
    if (i<len(adc_vals)//2):
      f=i
    # then start decreasing
    else:
      f-=1
    # scale the values to max 1024, then store
    adc_vals[i] = int((f/len(adc_vals))*1024.)

# scaling for ADC... full-scale is 1024, but it can also be reduced to make it amplified looking, (digital zoom with lower res.)
# TODO adjust from button/touchscreen? Maybe be able to adjust X stretch too?
adc_max_val = 1024.
adc_max_val = 128.

# call this after pulsing
def graph():
  global adc_vals
  global ssd
  global adc_max_val
  ssd.fill(1)
  ssd.fill(0)
  # figure out how many ADC samples will have to be averaged/filtered together
  chunk_size = len(adc_vals)//128
  # step through each chunk
  for i in range(0, len(adc_vals), chunk_size):
    avg = 0
    # loop through each value in this chunk
    for j in range(chunk_size):
      avg += adc_vals[i+j]
    # divide to get the average
    avg = avg//chunk_size
    # draw a line (x1,y1, x2,y2, color)
    ssd.framebuf.line(i//chunk_size, 64, i//chunk_size, 64-int((avg/adc_max_val*64.)), 1)
    # use this for inverted Y output
    # ssd.framebuf.line(i//chunk_size, 0, i//chunk_size, int((avg/adc_max_val*64.)), 1)
  ssd.show()


class OnePulseOverFlowCounter(object):
  def __init__(self, t1):
    self.longer_counter = 0
    self._longer_counter = 0
    self.tail_end = 0
    self.or_in_end = 0
    self.disable_cen_val = (~1) & 0xFFFF # disable CEN on ADC
    self.cr1 = stm.mem16[stm.TIM1 + stm.TIM_CR1] & (~1 & two_byte_mask)
    t1.callback(self.end_of_n_pulse_train__longer)

  def set_longer_counter(self, number_pulses):
    global number_of_pulse_pairs
    number_of_pulse_pairs = number_pulses
    self.cr1 = stm.mem16[stm.TIM1 + stm.TIM_CR1] & (~1 & two_byte_mask)
    if number_pulses is not None and number_pulses>128: # since RCR==0 yields one pulse, we SHOULD get an extra
      self.longer_counter = int((number_pulses-1) / 128.)
      self._longer_counter = self.longer_counter
      self.tail_end = (number_pulses % 128)
      self.or_in_end = (((self.tail_end*2)-1) & 0xff)
      # if self.tail_end==1 and self.longer_counter>1 and self.or_in_end>0:
      #  self.or_in_end -= 1
      
      #self.or_in_end = 0
      print('longer: {} tail: {} or in end: {}'.format(self.longer_counter, self.tail_end, self.or_in_end))
      self.or_in_end = ((stm.mem16[stm.TIM1 + stm.TIM_RCR] & 0xff<<8) 
                                             | self.or_in_end) 
      if self.tail_end == 1 and self.longer_counter<=1:
        adjust_tim1_pulses(127)
      else:
        adjust_tim1_pulses(128)
      # stm.mem16[stm.TIM1 + stm.TIM_CR1]  |= (0
      #  #| 0b11<<5  # center aligned
      #  | (1 << TIM_CR1_OPM)   # want one-time mode
      # )
      #stm.mem16[stm.TIM1 + stm.TIM_RCR] = stm.mem16[stm.TIM1 + stm.TIM_RCR] & 0xff<<8 # 0 RCR
      stm.mem16[stm.TIM1 + stm.TIM_CR1] &= (~(1<<TIM_CR1_OPM))&two_byte_mask # disable OPM
    else:#t1 = pyb.Timer(1, prescaler=common_prescaler, period=two_byte_mask, callback=end_of_n_pulse_train__longer)#end_of_n_pulse_train_pa1_first)
      stm.mem16[stm.TIM1 + stm.TIM_CR1]  |= (0
        #| 0b11<<5  # center aligned
        | (1 << TIM_CR1_OPM)   # want one-time mode
      )
      self.longer_counter = 0
      self._longer_counter = self.longer_counter
      print('longer: {} tail: {} pulses: {}'.format(self.longer_counter, self.tail_end, number_pulses))
      adjust_tim1_pulses(number_pulses)


  def end_of_n_pulse_train__longer(self, t):
    """ Writing the timer callback inside a Class allows us to have persistent data. TODO: is that true? do we need the Class?"""
    import stm
    if self.longer_counter == 0:
      stm.mem16[stm.TIM5 + stm.TIM_CR1] |= 0b1000 # enable OPM
      stm.mem16[stm.TIM2 + stm.TIM_CR1] |= 0b1000 # enable OPM
      stm.mem16[stm.TIM1 + stm.TIM_CR1] = self.cr1

#      stm.mem32[stm.GPIOB + stm.GPIO_ODR] = 0
      stm.mem16[stm.TIM4 + stm.TIM_CR1] &= self.disable_cen_val # disable CEN on ADC
    else:
      if self.longer_counter == 1:
          stm.mem16[stm.TIM1 + stm.TIM_CR1] |= 0b1000 # OPM
      elif self.longer_counter == 2:
          stm.mem16[stm.TIM1 + stm.TIM_RCR] = self.or_in_end

      self.longer_counter = (self.longer_counter - 1) & 0xFFFF


#t1 = pyb.Timer(1, prescaler=common_prescaler, period=two_byte_mask, callback=end_of_n_pulse_train__longer)#end_of_n_pulse_train_pa1_first)
rep_counter_overflow_detector = OnePulseOverFlowCounter(pyb.Timer(1, prescaler=common_prescaler, period=two_byte_mask))

tim2_channel = 3
tim2_3_out = pyb.Pin(pyb.Pin.cpu.A2, pyb.Pin.AF_PP, pyb.Pin.PULL_NONE, 1)  # PA2 set to AF1 --> TIM2_CH3
tim5_2_out = pyb.Pin(pyb.Pin.cpu.A1, pyb.Pin.AF_PP, pyb.Pin.PULL_NONE, 2)  # PA1 set to AF2 -->  TIM5_CH2

# enable_pb13_af_and_connect_to_tim1()  2018-7-16-jg

# as long as both TIM's tick at AHB freq, the TIM's will tick at the same rate;
# should there be any APB divider impacting TIM input clock freq,
# this has to be factored in (individually per timer, as they are on different APBs)


def a(period, width, number_pulses=None):
  """ adjust the HV pulser's pulse-to-pulse period, pulse width, and number of push-pull pulse-pairs """
  global number_of_pulse_pairs
  global tim2_channel
  number_of_pulse_pairs = number_pulses
  adjust_tim5(period, width)
  adjust_tim2(period, width, tim2_channel)
  adjust_tim1(period, period//2, number_pulses)
  rep_counter_overflow_detector.set_longer_counter(number_pulses)

def q(num):
  """ adjust number of pulses for quick-pulsing that seems to produce HV low ripple """
  a(150,4,num)
  pulse()

# aa, b, and c are functions that I used during debug of overflow detection
# (N-pulse counter can hold 255, since we have pairs, that is 127 pairs)... so this was testing the interface of overflow
def aa():
  a(150,4,127)
  pulse()

def b():
  a(44,20,8)
  pulse()

def c():
  a(150,4,129)
  pulse()

def d():
  aa();pulse()
  b();pulse()
  c();pulse()


# rewrite setup_slave_timer() to include chunk of 8 bits CCMR settings including pwm mode.
# chunk of 8 bits CCMR settings ==>  OCxCE_OCxM_OCxPE_OCxFE_CCxS parameter
slave_tim = setup_slave_timer('TIM5', 2, 'TIM3', common_prescaler, period, width)
slave_tim = setup_slave_timer('TIM2', tim2_channel, 'TIM3', common_prescaler, period, width)
tim_kickoff = setup_n_pulse_kickoff_timer("TIM3", 1, common_prescaler, period, width)


# now setup TIM1 - we want it to disable itself i.e. one-pulse mode; 3 pulses, that goes to repetition counter - as the window is cca 600ms, let make them 50ms ON / 50ms OFF
stm.mem16[stm.TIM1 + stm.TIM_PSC] = common_prescaler
adjust_tim1(period=period, width=period//2, number_pulses=number_of_pulse_pairs)

# 15 14 13 12 11 10 9 8 7 6   5    4    3    2    1    0
# Reserved                TG  Res. CC4G CC3G CC2G CC1G UG
TIM_EGR_UG = 1
#stm.mem16[stm.TIM1 + stm.TIM_EGR] = TIM_EGR_UG         # through forced update load prescaler from shadow
# (CCMR1)
# 15     14 13 12   11    10     9 8      7    6 5 4      3     2      1 0
# OC2CE OC2M[2:0] OC2PE OC2FE CC2S[1:0] OC1CE OC1M[2:0] OC1PE OC1FE CC1S[1:0]

stm.mem16[stm.TIM1 + stm.TIM_CCMR1] = (0
  | (TIM_CCMR_CCS__OUTPUT << TIM_CCMR1_CC1S_0)  # output compare
  | (TIM_CCMR_OCM__PWM2   << TIM_CCMR1_OC1M_0))

#3     2  
#CC1NP CC1NE
TIM_CCER_CC1NP = 3
TIM_CCER_CC1NE = 2
TIM_CCER_CC1P = 1
TIM_CCER_CC1E = 0
stm.mem16[stm.TIM1 + stm.TIM_CCER] |= (0
  #| (1 << TIM_CCER_CC1P)
  #| (1 << TIM_CCER_CC1NP)  # invert it to compensate for it being the CHxN channel (we might have selected the other PWM mode in CCMR as well)
  | (1 << TIM_CCER_CC1NE))  # enable TIM1_CH1N
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

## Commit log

2017-01-06 set up repo from JGs project dir
    [diode-SPICE_param_calc.ods, diode_modeling-2500.ods, diode_modeling-r3000.ods, diode_modeling.ods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]
2017-01-15 sym/NFET_enh.sym sym/PFET_enh.sym sym/USB_SMT_5p.sym sym/ffc-zif-20.sym sym/ffc-zif-6.sym
    [shock_kvboard.sch]
2017-01-17 stm32f401ce footprint with paste proper, tidy and siz minimize sketches
    [shock_kvboard.sch]
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2017-01-29 improved STM32F401Cx symbol
    [shock_kvboard.sch, shock_micropulser.sch]
2017-01-29 kvboard work -- parts, bom
    [shock_micropulser.sch]
2017-01-29 shortened names kvboard.sch micropulser.sch preparing for makefile use
    [kvboard.sch, micropulser.sch]
2017-02-03 kvboard new parts
    [kvboard.sch]
2017-02-05 added footprints disk_cap_5mm_flat.fp cap_10mm_alum_smt.fp, tuned DC-05-jack.fp SOT223_NXP.fp xfmr_epc19_10.fp for mfrability, renamed simul dir for clarity
    [diode-SPICE_param_calc.ods, diode_modeling-2500.ods, diode_modeling-r3000.ods, diode_modeling.ods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]
2017-02-06 remove duplicate copy of gnucap-example-jb -- it is available on the web
    [mycircuit.sch, simplefilter.sch, voltagedoubler.sch]
2017-02-07 more kvboard details
    [kvboard.sch]
2017-02-07 copy symbols from lib to project symbols
    [kvboard.sch, micropulser.sch]
2017-02-08 schematic progress, png schematic images update
    [micropulser.sch]
2017-02-09 schematic details, G30_TH adater board called g30pulser.sch
    [g30pulser.sch, kvboard.sch, micropulser.sch]
2017-02-10 edited symbols for pwr, added back Vdd:1 format taken out by mistake, USB_SMT_5p.sym Vdd.sym crystal-2.sym stm32f401cx.sym drc check passed on micropulser.sch kvboard.sch g30pulser.sch, first cut at 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
    [g30pulser.bom.csv, g30pulser.sch, kvboard.bom.csv, kvboard.sch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]
2017-02-10 BOMs in makefile, change BOM file extension to .bom.tsv
    [g30pulser.bom.tsv, kvboard.bom.tsv, micropulser.bom.tsv]
2017-02-11 edited/added footprints 1206_HV.fp disk_cap_5mm_flat.fp SOT23-123.fp SOT23-GDS.fp header20single.fp ../../g30pulser.lht more detail on schematics, makefile, BOMs
    [g30pulser.bom.tsv, g30pulser.sch, kvboard.bom.tsv, kvboard.sch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]
2017-02-12 schematics pass drc, makefile generates bom, netlist -- time to check, then layout
    [g30pulser.bom.tsv, g30pulser.sch, kvboard.bom.tsv, kvboard.sch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]
2017-02-12 added .png schematic images
    [kvboard.sch]
2017-02-13 added DC-0500.fp ffc_zif_20.fp push_b_6mm.fp spring_coin_contact.fp spring_side_contact.fp, improved xfmr_epc19_10.fp microUSB_AB_1.fp disk_cap_5mm_flat.fp diode_10mm.fp cap_10mm_alum_smt.fp 2x5hdr_1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
    [g30pulser.sch, kvboard.sch, micropulser.sch]
2017-02-13 made pngs of some part dawings
    [kvboard.bom.tsv]
2017-02-14 added DC-0500.fp diode_10mm.fp spring_coin_contact.fp disk_cap_5mm_flat_flip.fp DC_jack.sym nmos-4pad.sym to take care of layout discrepancies, started layout of kvboard
    [g30pulser.bom.tsv, kvboard.bom.tsv, kvboard.sch, micropulser.bom.tsv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]
2017-02-16 boards at v0.1 as sent to fab, ( almost...)
    [g30pulser.bom.tsv, g30pulser.sch, kvboard.bom.tsv, kvboard.sch]
2017-02-22 as built documenting of ceramic caps used on v0.1
    [g30pulser.bom.tsv, g30pulser.sch, kvboard.bom.tsv, kvboard.sch]
2017-04-19 v0.1 as built g30pulser plus correction of wrong AP2120N footprint
    [g30pulser.sch]
2017-04-20 readbility of 3.3V near AP2120N symbol
    [g30pulser.sch]
2017-04-22 moved hardware design files to a folder named hardware_schematics_layouts
    [g30pulser.bom.tsv, g30pulser.sch, kvboard.bom.tsv, kvboard.sch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]
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2017-04-22 new dir called micropython_low_level_timer_control_code
    [pins.csv]
2017-04-22 renamed micropython_low_level_timer_control_code shorter so it shows in github view
    [pins.csv]
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2017-04-23 changed cable twist between boards micropulser.sch and kvboard.sch, corrected volt reg package mistake both boards.
    [g30pulser.sch, micropulser.sch]
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2017-07-18 profiles of back and front of enclosure clamshell .step
    [cs-enc-back-edgesweep-1.step, cs-enc-front-edgesweep-1.step]
2017-08-13 g30pulser.schv0.3 kvboard.schv0.2
    [cs-enc-back-edgesweep-1.step, cs-enc-back-perim-5mm-1.fcstd, cs-enc-back-perim.fcstd, g30pulser.sch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]
2017-08-16 g30pulser v 0.3 kvboard v 0.2 as sent to fab
    [g30pulser.sch, kvboard.sch]
2017-09-02 kvboard 0.2, g30pulser 0.3 as sent to fab
    [cs-enc-back-perim-5mm-1.fcstd, g30pulser.bom.assy.ods, g30pulser.bom.tsv, kvboard.bom.assy.ods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]
2017-09-09 enclosure parametrics
    [cs-enc-part-cont-bottom-1.fcstd, cs-enc-part-cont-bottom-2.fcstd, cs-enc-shapebinder-1.fcstd, cs-enc-spread-driven-1.fcstd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]
2017-09-21 enclosure 3D work, g30_pulser_v0.2 misc.
    [cs-enc-back-bathtub-drafted.fcstd, cs-enc-back-sketch.fcstd, cs-enc-back-swept-4.9mm-1.fcstd, cs-enc-part-cont-bottom-1-redo-example.fcstd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]
2017-10-05 Adding symbols, footprints as micropulser with 3) boost switchers is made, correcting smb-min.fp backwards
    [micropulser.sch]
2017-10-12 micropulser partial as of 2017-10-10
    [micropulser.bom.tsv, micropulser.sch]
2017-10-12 using PYFLEX_F401 noted on schematic.
    [micropulser.sch]
2017-10-17 subcircuit footprints for practical use on next rev.
    [kvboard.sch]
2017-10-21 New footprints.
    [kvboard.sch]
2017-10-22 micropulser.sch added TP5000, cleanup footprints lib
    [micropulser.sch]
2017-10-29 UFQFPN48-min.lht footprint improved far side connection to center pad
    [micropulser.sch]
2017-11-06 footprints for crystals and power converters refined in schematic
    [micropulser.sch]
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2017-11-18 added detail part numbers and footprints to micropulser.sch
    [micropulser.sch]
2017-11-19 pyflex_f401.sch renamed from micropulser.sch and related.
    [kvboard.bom.tsv, pyflex_f401.bom.tsv, pyflex_f401.sch]
2017-11-19 rename dirs for clarity, G30TH obsolescence
    [pins.csv]
2017-11-22 rename_dirs added pyflex_mcu_code for new platform, etc.
    [pins.csv]
2017-11-29 prep for new platform STM32F401CE names adn alt functions.
    [pyflex_f401.sch, pyflex_f401_STM32F401CE_AF_AltFuncList-portA.ods, pyflex_f401_STM32F401CE_AF_AltFuncList-portB.ods]
2017-11-30 pyflex_f401.sch more names, compacted symbol stm32f401ce.sym
    [pyflex_f401.sch]
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2017-12-02 pyflex_f401.sch and mpconfigboard.h partial board definition
    [pyflex_f401.sch, pyflex_f401_STM32F401CE_AF_AltFuncList-portA.ods, pyflex_f401_STM32F401CE_AF_AltFuncList-portB.ods]
2017-12-02 pyflex_f401.sch board definition USB details
    [pyflex_f401.sch]
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2018-01-13 SOT23-5N.lht correction, fit into DC-DC layout cell, add regulator_TLV702.sym.
    [pyflex_f401.bom.tsv, pyflex_f401.sch]
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2018-01-14 Schematic netlist fixes pyflex_f401_boost.sym had a mistake.
    [pyflex_f401.bom.tsv, pyflex_f401.sch, pyflex_f401_boost.bom.tsv, pyflex_f401_boost.sch]
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2018-01-14 TP5000 symbol fix, SWITCH_PB_NO_4MM.sym, SWITCH_4mm.lht footprint.
    [pyflex_f401.bom.tsv, pyflex_f401.sch]
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2018-01-15 Fix symbol cuvette_cont.sym.
    [kvboard.sch]
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2018-01-27 Layout progress on kvboard analog power and HV. Fixed some footprint problems, improved xfmr footprint.
    [kvboard.bom.tsv, kvboard.sch, pyflex_f401.bom.tsv, pyflex_f401.sch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]
2018-01-29 Layout progress on kvboard 75% needs outline decided. pyflex_f401 is 40%, so it won't get tight in time for the deadline.
    [kvboard.bom.tsv, kvboard.sch, pyflex_f401.sch, pyflex_f401_all.bom.tsv]
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2018-02-14 Fix mistakes in BOMs, assembly drawings, schematics.
    [pyflex_f401.bom.tsv, pyflex_f401.sch, pyflex_f401_all.bom.tsv, pyflex_f401_boost.sch]
2018-02-25 Fix layout footprint mistakes and do XTAL symmetry and ground plane. 1.
    [pyflex_f401.sch, pyflex_f401_all.bom.tsv]
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2018-03-16 update mistaken transistors Q3 Q6 Q9 --> BC817W SOT-323, Q31 Q41 --> BC857BWT1G SOT-323. Fix wrong symbol used in schematic for Q3 Q6 Q9.
    [pyflex_f401.sch, pyflex_f401_all.bom.tsv, pyflex_f401_boost.sch]
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2018-03-24 Changed TXFMR_EPC19.lht, but still drc problems, kvboard.lht improved HV area outline.
    [pyflex_f401.sch]
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2018-04-15 Frozen test with G30TH fails.
    [kvboard.sch, pyflex_f401.sch]
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2018-05-29 Comment about U1 fall time fix needed on kvboard.sch.
    [kvboard.sch]
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2018-07-01 pyflex_f401.lht pyflex_f401_boost.sch silk-fixes-2.
    [pyflex_f401_boost.sch]
2018-07-01 Save v0.6 versions of schematics and layout for using as built boards, begin adding fixes as v0.7-rc1.
    [kvboard_v0.6.sch, pyflex_f401_boost.sch, pyflex_f401_v0.6.sch]
2018-07-01 Save pyflex_f401_boost_v0.6.sch, pyflex_f401.lht fixes to R43 R47 as v0.7-rc1.
    [pyflex_f401_boost_v0.6.sch]
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2018-07-24 Fixed swapped signal name of PA2, PA1, NPA1, NPA2 at U5.
    [pyflex_f401.sch]
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2018-12-13 Rearranged history of enclosure experiments in old directory, latest is shorter name cs-enc-15c.fcstd.
    [FC017_Body_with_Draft_Polygon.fcstd, Fillet--pipe-b-spline.fcstd, cs-enc-15c.fcstd, cs-enc-back-bathtub-drafted.fcstd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]
2019-03-13 Rearranged enclosure recent work, some into a broken status directory.
    [cs-enc-15d.fcstd, cs-enc-15e.fcstd, cs-enc-spread-driven-09broken.fcstd, cs-enc-spread-driven-09c4broken.fcstd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]
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
